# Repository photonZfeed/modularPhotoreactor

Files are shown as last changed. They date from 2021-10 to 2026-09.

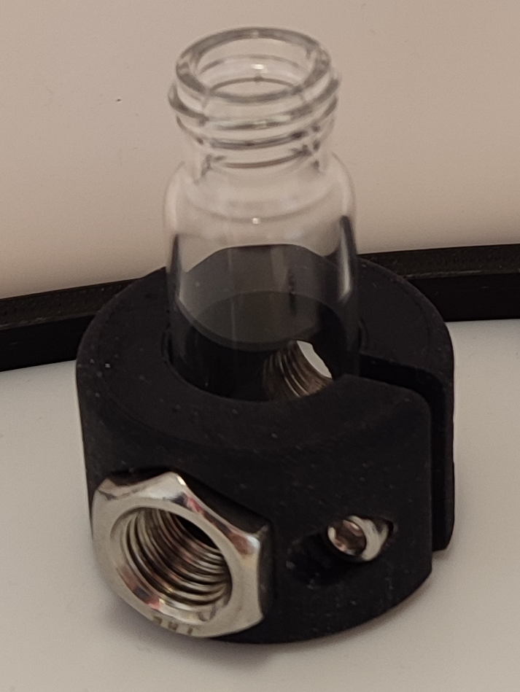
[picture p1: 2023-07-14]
01_CAD/03_Multi_Batch_Screening_Photoreactor/00_Indirect_Irradiation_Module/04_Accesories/00_UV_Vis_Cell_4mL_GC_Vial/UV_vis_cell_4mL_GC_vial_SLA.png

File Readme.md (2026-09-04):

# modularPhotoreactor

A modular and characterized open source photoreactor and the mutli-batch screening phototreactor extension

## Documentation

The assembly of the devices is documented in the [CAD section](./01_CAD/).

See also the 3D-pdfs for detailed assembly instructions in the [assembly section](./03_ASSEMBLY_INSTRUCTIONS/).

The Python modules for the operation of the reactor controller are documented in the repository [Py4ModPhotoreactor](https://github.com/photonZfeed/Py4ModPhotoreactor). See also the fairly detailed docstrings in the code. 

## Folder Structure

```
📦HARDWARE_Modular_Photoreactor
┣ 📂 01_CAD
┃  ┣ 📂 00_Corpus
┃  ┃  ┣ 📂 00_Corpus_90x90x100mm
┃  ┃  ┃  ┣ 📂 00_corpus
┃  ┃  ┃  ┃  ┣ 📜 corpus_90x90x100mm_back_wall.stl
┃  ┃  ┃  ┃  ┣ 📜 corpus_90x90x100mm_front_wall.stl
┃  ┃  ┃  ┃  ┣ 📜 corpus_90x90x100mm_side_walls.stl
┃  ┃  ┃  ┃  ┣ 📜 corpus_90x90x100mm_side_walls_LED_holder.stl
┃  ┃  ┃  ┃  ┣ 📜 corpus_cover.stl
┃  ┃  ┃  ┃  ┗ 📜 corpus_stand.stl
┃  ┃  ┃  ┣ 📂 01_irradiation_module
┃  ┃  ┃  ┃  ┣ 📜 20210104_Thorlabsl_modul.stl
┃  ┃  ┃  ┃  ┣ 📜 corpus_90x90mm_irrad_Max350.stl
┃  ┃  ┃  ┃  ┣ 📜 corpus_90x90mm_irrad_Max350_adapter.stl
┃  ┃  ┃  ┃  ┣ 📜 corpus_90x90mm_irrad_starcool.stl
┃  ┃  ┃  ┃  ┣ 📜 corpus_90x90mm_irrad_Thorlabs.stl
┃  ┃  ┃  ┃  ┣ 📜 corpus_90x90mm_irrad_Thorlabs_adapter.stl
┃  ┃  ┃  ┃  ┗ 📜 corpus_90x90mm_irrad_Thorlabs_collimator.stl
┃  ┃  ┃  ┣ 📂 02_stirring_module
┃  ┃  ┃  ┃  ┣ 📜 corpus_90x90mm_stirring_module.stl
┃  ┃  ┃  ┃  ┣ 📜 corpus_90x90mm_stirring_module_holder_electric_motor.stl
┃  ┃  ┃  ┃  ┣ 📜 corpus_90x90mm_stirring_module_magnet_holder.stl
┃  ┃  ┃  ┃  ┗ 📜 corpus_90x90mm_stirring_module_magnet_holder_blind_plug.stl
┃  ┃  ┃  ┗ 📂 03_sample_holders
┃  ┃  ┃     ┣ 📜 corpus_90x90mm_11mL_Biotage_MWvial_6S_alignment_holder.stl
┃  ┃  ┃     ┣ 📜 corpus_90x90mm_11mL_Biotage_MWvial_6S_holder.stl
┃  ┃  ┃     ┣ 📜 corpus_90x90mm_4mL_GCvial_ND13_10S_alignment_holder.stl
┃  ┃  ┃     ┣ 📜 corpus_90x90mm_4mL_GCvial_ND13_10S_holder.stl
┃  ┃  ┃     ┣ 📜 corpus_90x90mm_4mL_GCvial_ND13_1S_alignment_holder.stl
┃  ┃  ┃     ┣ 📜 corpus_90x90mm_4mL_GCvial_ND13_1S_holder.stl
┃  ┃  ┃     ┣ 📜 corpus_90x90mm_4mL_GCvial_ND13_4S_alignment_holder.stl
┃  ┃  ┃     ┣ 📜 corpus_90x90mm_4mL_GCvial_ND13_4S_holder.stl
┃  ┃  ┃     ┣ 📜 corpus_90x90mm_4mL_GCvial_ND13_6S_alignment_holder.stl
┃  ┃  ┃     ┣ 📜 corpus_90x90mm_4mL_GCvial_ND13_6S_holder.stl
┃  ┃  ┃     ┣ 📜 corpus_90x90mm_4mL_GCvial_ND13_8S_alignment_holder.stl
┃  ┃  ┃     ┣ 📜 corpus_90x90mm_4mL_GCvial_ND13_8S_holder.stl
┃  ┃  ┃     ┣ 📜 corpus_90x90mm_8mL_GCvial_ND13_10S_alignment_holder.stl
┃  ┃  ┃     ┗ 📜 corpus_90x90mm_8mL_GCvial_ND13_1S_alignment_holder.stl
┃  ┃  ┣ 📂 01_Corpus_90x90x140mm
┃  ┃  ┃  ┣ 📂 00_corpus
┃  ┃  ┃  ┃  ┣ 📜 corpus_90x90x140mm_back_wall.stl
┃  ┃  ┃  ┃  ┣ 📜 corpus_90x90x140mm_front_wall.stl
┃  ┃  ┃  ┃  ┣ 📜 corpus_90x90x140mm_side_walls.stl
┃  ┃  ┃  ┃  ┣ 📜 corpus_cover.stl
┃  ┃  ┃  ┃  ┗ 📜 corpus_stand.stl
┃  ┃  ┃  ┣ 📂 01_irradiation_module
┃  ┃  ┃  ┃  ┣ 📜 20210104_Thorlabsl_modul.stl
┃  ┃  ┃  ┃  ┣ 📜 corpus_90x90mm_irrad_Max350.stl
┃  ┃  ┃  ┃  ┣ 📜 corpus_90x90mm_irrad_Max350_adapter.stl
┃  ┃  ┃  ┃  ┣ 📜 corpus_90x90mm_irrad_starcool.stl
┃  ┃  ┃  ┃  ┣ 📜 corpus_90x90mm_irrad_Thorlabs.stl
┃  ┃  ┃  ┃  ┣ 📜 corpus_90x90mm_irrad_Thorlabs_adapter.stl
┃  ┃  ┃  ┃  ┗ 📜 corpus_90x90mm_irrad_Thorlabs_collimator.stl
┃  ┃  ┃  ┣ 📂 02_stirring_module
┃  ┃  ┃  ┃  ┣ 📜 corpus_90x90mm_stirring_module.stl
┃  ┃  ┃  ┃  ┣ 📜 corpus_90x90mm_stirring_module_holder_electric_motor.stl
┃  ┃  ┃  ┃  ┣ 📜 corpus_90x90mm_stirring_module_magnet_holder.stl
┃  ┃  ┃  ┃  ┗ 📜 corpus_90x90mm_stirring_module_magnet_holder_blind_plug.stl
┃  ┃  ┃  ┗ 📂 03_sample_holders
┃  ┃  ┃     ┣ 📜 corpus_90x90mm_11mL_Biotage_MWvial_6S_alignment_holder.stl
┃  ┃  ┃     ┣ 📜 corpus_90x90mm_11mL_Biotage_MWvial_6S_holder.stl
┃  ┃  ┃     ┣ 📜 corpus_90x90mm_4mL_GCvial_ND13_10S_alignment_holder.stl
┃  ┃  ┃     ┣ 📜 corpus_90x90mm_4mL_GCvial_ND13_10S_holder.stl
┃  ┃  ┃     ┣ 📜 corpus_90x90mm_4mL_GCvial_ND13_1S_alignment_holder.stl
┃  ┃  ┃     ┣ 📜 corpus_90x90mm_4mL_GCvial_ND13_1S_holder.stl
┃  ┃  ┃     ┣ 📜 corpus_90x90mm_4mL_GCvial_ND13_4S_alignment_holder.stl
┃  ┃  ┃     ┣ 📜 corpus_90x90mm_4mL_GCvial_ND13_4S_holder.stl
┃  ┃  ┃     ┣ 📜 corpus_90x90mm_4mL_GCvial_ND13_6S_alignment_holder.stl
┃  ┃  ┃     ┣ 📜 corpus_90x90mm_4mL_GCvial_ND13_6S_holder.stl
┃  ┃  ┃     ┣ 📜 corpus_90x90mm_4mL_GCvial_ND13_8S_alignment_holder.stl
┃  ┃  ┃     ┣ 📜 corpus_90x90mm_4mL_GCvial_ND13_8S_holder.stl
┃  ┃  ┃     ┣ 📜 corpus_90x90mm_8mL_GCvial_ND13_10S_alignment_holder.stl
┃  ┃  ┃     ┗ 📜 corpus_90x90mm_8mL_GCvial_ND13_1S_alignment_holder.stl
┃  ┃  ┗ 📂 02_Corpus_130x130x130mm
┃  ┃     ┣ 📂 00_corpus
┃  ┃     ┃  ┣ 📜 corpus130x130mm_side_walls.stl
┃  ┃     ┃  ┣ 📜 corpus_130x130mm_back_wall.stl
┃  ┃     ┃  ┣ 📜 corpus_130x130mm_cover.stl
┃  ┃     ┃  ┣ 📜 corpus_130x130mm_front_wall_monting_thermal_hose.stl
┃  ┃     ┃  ┣ 📜 corpus_130x130mm_side_wall_left.stl
┃  ┃     ┃  ┣ 📜 corpus_130x130mm_side_wall_right.stl
┃  ┃     ┃  ┣ 📜 corpus_130x130mm_stand_20mm.stl
┃  ┃     ┃  ┣ 📜 fin_back_wall.stl
┃  ┃     ┃  ┣ 📜 fin_front_wall.stl
┃  ┃     ┃  ┣ 📜 spacer_side_walls_5mm.stl
┃  ┃     ┃  ┗ 📜 spacer_stand_5mm.stl
┃  ┃     ┣ 📂 01_irradiation_module
┃  ┃     ┃  ┗ 📜 irrad_module.stl
┃  ┃     ┣ 📂 02_sample_holders
┃  ┃     ┃  ┣ 📜 corpus_130x130mm_GCvial_ND13_18S_alignment_holder.stl
┃  ┃     ┃  ┣ 📜 corpus_130x130mm_GCvial_ND13_18S_holder.stl
┃  ┃     ┃  ┣ 📜 corpus_130x130mm_GCvial_ND13_1S_alignment_holder.stl
┃  ┃     ┃  ┗ 📜 corpus_130x130mm_GCvial_ND13_1S_holder.stl
┃  ┃     ┗ 📂 03_tempering_module
┃  ┃        ┣ 📜 back_mounting_thermo_hose.stl
┃  ┃        ┣ 📜 fan_holder.stl
┃  ┃        ┣ 📜 holder_tempering_module.stl
┃  ┃        ┣ 📜 mounting_alu_water_cooler.stl
┃  ┃        ┗ 📜 spacer_holder_tempering_module.stl
┃  ┣ 📂 01_controller
┃  ┃  ┣ 📜 controller_case.stl
┃  ┃  ┣ 📜 controller_case_LCD_holder.stl
┃  ┃  ┗ 📜 controller_electronic_board_holder.stl
┃  ┣ 📂 02_Peripheral_Modules
┃  ┃  ┣ 📂 00_ambient_temperature
┃  ┃  ┃  ┣ 📜 base_plate_ambient_temperature_extension.stl
┃  ┃  ┃  ┗ 📜 case_ambient_temperature_extension.stl
┃  ┃  ┣ 📂 01_tempering_extension
┃  ┃  ┃  ┣ 📜 base_plate.stl
┃  ┃  ┃  ┗ 📜 case_tempering_extension.stl
┃  ┃  ┣ 📂 02_master_extension
┃  ┃  ┃  ┣ 📜 base_plate.stl
┃  ┃  ┃  ┗ 📜 case_master_extension.stl
┃  ┃  ┣ 📂 03_membrane_pump_extension
┃  ┃  ┃  ┣ 📜 base_plate_membrane_pump.stl
┃  ┃  ┃  ┣ 📜 base_plate_membrane_pump_exension.stl
┃  ┃  ┃  ┣ 📜 case_membrane_pump.stl
┃  ┃  ┃  ┗ 📜 case_membrane_pump_extension.stl
┃  ┃  ┗ 📂 04_pressure_sensor_extension
┃  ┃     ┣ 📜 base_plate.stl
┃  ┃     ┣ 📜 base_plate_updated.stl
┃  ┃     ┣ 📜 case_pressure_extension.stl
┃  ┃     ┗ 📜 case_pressure_extension_updated.stl
┃  ┣ 📂 03_Multi_Batch_Screening_Photoreactor
┃  ┃  ┣ 📂 00_Indirect_Irradiation_Module
┃  ┃  ┃  ┣ 📂 00_Base_Module
┃  ┃  ┃  ┃  ┗ 📜 Base_Module.stl
┃  ┃  ┃  ┣ 📂 01_Irradiation_Module
┃  ┃  ┃  ┃  ┣ 📜 300mm_alu_heatsink.stl
┃  ┃  ┃  ┃  ┣ 📜 heatsink_holder_left.stl
┃  ┃  ┃  ┃  ┣ 📜 heatsink_holder_right.stl
┃  ┃  ┃  ┃  ┗ 📜 stand_irradiation_module.stl
┃  ┃  ┃  ┣ 📂 02_Reflector_Module
┃  ┃  ┃  ┃  ┣ 📜 PTFE_Side_Wall.stl
┃  ┃  ┃  ┃  ┣ 📜 Reflector_Holder_Nut.stl
┃  ┃  ┃  ┃  ┗ 📜 Reflector_Holder_Screw.stl
┃  ┃  ┃  ┣ 📂 03_Mobile_Cover
┃  ┃  ┃  ┃  ┣ 📜 back.stl
┃  ┃  ┃  ┃  ┣ 📜 connector.stl
┃  ┃  ┃  ┃  ┣ 📜 front.stl
┃  ┃  ┃  ┃  ┣ 📜 sides.stl
┃  ┃  ┃  ┃  ┗ 📜 top.stl
┃  ┃  ┃  ┗ 📂 04_Accesories
┃  ┃  ┃     ┗ 📂 00_UV_Vis_Cell_4mL_GC_Vial
┃  ┃  ┃        ┣ 📜 UV_vis_cell_4mL_GC_vial_SLA.png
┃  ┃  ┃        ┗ 📜 UV_vis_cell_4mL_GC_vial_SLA.stl
┃  ┃  ┗ 📂 01_Direct_Irradiation_Module
┃  ┃     ┣ 📂 00_reflector_fixed_height
┃  ┃     ┃  ┣ 📜 corner_pillar_1.stl
┃  ┃     ┃  ┣ 📜 corner_pillar_2.stl
┃  ┃     ┃  ┣ 📜 corner_pillar_3.stl
┃  ┃     ┃  ┣ 📜 corner_pillar_4.stl
┃  ┃     ┃  ┣ 📜 corner_pillar_connector_330mm.stl
┃  ┃     ┃  ┣ 📜 corner_pillar_connector_350mm.stl
┃  ┃     ┃  ┣ 📜 corner_pillar_support.stl
┃  ┃     ┃  ┣ 📜 heatsink_holder_female.stl
┃  ┃     ┃  ┣ 📜 heatsink_holder_male.stl
┃  ┃     ┃  ┣ 📜 holder_feet.stl
┃  ┃     ┃  ┣ 📜 holder_feet_assembly.stl
┃  ┃     ┃  ┣ 📜 holder_feet_support.stl
┃  ┃     ┃  ┣ 📜 reflector_fixed_height_assembly.stl
┃  ┃     ┃  ┗ 📜 reflector_holder.stl
┃  ┃     ┣ 📂 01_modular_reflector_adjustable_height
┃  ┃     ┃  ┣ 📜 corner_reflector_holder_1a.stl
┃  ┃     ┃  ┣ 📜 corner_reflector_holder_1b.stl
┃  ┃     ┃  ┣ 📜 modular_reflector_assembly.stl
┃  ┃     ┃  ┣ 📜 reflector_holder_330mm_1cm.stl
┃  ┃     ┃  ┣ 📜 reflector_holder_330mm_2cm.stl
┃  ┃     ┃  ┣ 📜 reflector_holder_330mm_6cm.stl
┃  ┃     ┃  ┣ 📜 reflector_holder_350mm_1cm.stl
┃  ┃     ┃  ┣ 📜 reflector_holder_350mm_2cm.stl
┃  ┃     ┃  ┗ 📜 reflector_holder_350mm_6cm.stl
┃  ┃     ┗ 📂 02_heatsink_and _LED_mounting_plate
┃  ┃        ┣ 📜 heatsink_200x200.stl
┃  ┃        ┗ 📜 LED_mount_400x400.stl
┃  ┗ 📜 readme.md
┣ 📂 02_MATERIALS
┃  ┣ 📂 00_electronics
┃  ┃  ┣ 📂 00_Tinkerforge
┃  ┃  ┃  ┗ 📜 Tinkerforge.txt
┃  ┃  ┣ 📂 01_LEDs
┃  ┃  ┃  ┣ 📂 blue
┃  ┃  ┃  ┃  ┣ 📂 453nm
┃  ┃  ┃  ┃  ┃  ┗ 📜 LZ4-00B208-0000.txt
┃  ┃  ┃  ┃  ┣ 📂 455nm
┃  ┃  ┃  ┃  ┃  ┗ 📜 LST1-01F06-RYL1-00.txt
┃  ┃  ┃  ┃  ┗ 📂 460nm
┃  ┃  ┃  ┃     ┣ 📜 5412869-LED_2520Engin_Datasheet_LuxiGen_LZ1-00DB00-1532005.pdf
┃  ┃  ┃  ┃     ┗ 📜 LZ1-00DB00.txt
┃  ┃  ┃  ┣ 📂 green
┃  ┃  ┃  ┃  ┗ 📂 530nm
┃  ┃  ┃  ┃     ┗ 📜 LST1-01F06-GRN1-00.txt
┃  ┃  ┃  ┣ 📂 RGBA
┃  ┃  ┃  ┃  ┗ 📜 LZ4-20MA00-0000.txt
┃  ┃  ┃  ┗ 📂 UV
┃  ┃  ┃     ┣ 📂 365nm
┃  ┃  ┃     ┃  ┗ 📜 LST1-01G01-UV01-00.txt
┃  ┃  ┃     ┣ 📂 385nm
┃  ┃  ┃     ┃  ┗ 📜 LZ1-10UB00-01U4.txt
┃  ┃  ┃     ┗ 📂 405nm
┃  ┃  ┃        ┣ 📂 onecore
┃  ┃  ┃        ┃  ┗ 📜 LZ1-10UB00-01U7.txt
┃  ┃  ┃        ┗ 📂 quadcore
┃  ┃  ┃           ┗ 📜 LZ4-V0UB0R-00U8.txt
┃  ┃  ┣ 📂 02_raspberry_pi
┃  ┃  ┃  ┗ 📜 raspberry_pi_4_8GB.txt
┃  ┃  ┣ 📂 03_sd_card
┃  ┃  ┃  ┗ 📜 SD_card.txt
┃  ┃  ┣ 📂 04_peltier_element
┃  ┃  ┃  ┗ 📜 peltier.txt
┃  ┃  ┣ 📂 05_power_supplies
┃  ┃  ┃  ┣ 📂 00_12V_5A
┃  ┃  ┃  ┃  ┗ 📜 12V_5A.txt
┃  ┃  ┃  ┗ 📂 00_24V_6A
┃  ┃  ┃     ┗ 📜 24V_6A.txt
┃  ┃  ┣ 📂 06_small_parts
┃  ┃  ┃  ┣ 📂 00_stripboard
┃  ┃  ┃  ┃  ┗ 📜 stripboard_WR_914-HP.txt
┃  ┃  ┃  ┣ 📂 01_connection_jacks
┃  ┃  ┃  ┃  ┣ 📜 2Pin_PCB_Mount_2.5mm_Pitch.txt
┃  ┃  ┃  ┃  ┣ 📜 2Pin_PCB_Mount_5mm_Pitch.txt
┃  ┃  ┃  ┃  ┣ 📜 banana_plug_female.txt
┃  ┃  ┃  ┃  ┣ 📜 banana_plug_male.txt
┃  ┃  ┃  ┃  ┣ 📜 Cable_extension_PWM_4-Pin_Moltex.txt
┃  ┃  ┃  ┃  ┣ 📜 DC_Jack.txt
┃  ┃  ┃  ┃  ┗ 📜 wago_2Conductur_clamp.txt
┃  ┃  ┃  ┣ 📂 02_Stacking_Header_Raspberry_Pi
┃  ┃  ┃  ┃  ┗ 📜 Stacking_Header_Raspberry_Pi.txt
┃  ┃  ┃  ┣ 📂 03_two_position_switch
┃  ┃  ┃  ┃  ┗ 📜 two_position_switch.txt
┃  ┃  ┃  ┗ 📂 04_silicone_wire
┃  ┃  ┃     ┗ 📜 silicone_wire.txt
┃  ┃  ┣ 📂 07_LED_drivers
┃  ┃  ┃  ┣ 📜 350mA_driver.txt
┃  ┃  ┃  ┣ 📜 500mA_driver.txt
┃  ┃  ┃  ┗ 📜 700mA_driver.txt
┃  ┃  ┣ 📂 08_membrane_pump
┃  ┃  ┃  ┣ 📜 accessories_membrane_pump.txt
┃  ┃  ┃  ┗ 📜 Membrane_Pump.txt
┃  ┃  ┗ 📂 09_fans
┃  ┃     ┣ 📂 00_fan_corpus_90x90mm
┃  ┃     ┃  ┗ 📜 fan.txt
┃  ┃     ┣ 📂 01_fan_corpus_130x130mm
┃  ┃     ┃  ┣ 📜 fan.txt
┃  ┃     ┃  ┗ 📜 fan_update.txt
┃  ┃     ┣ 📂 02_power_supply_fan_corpus_90x90mm
┃  ┃     ┃  ┗ 📜 power_supply.txt
┃  ┃     ┗ 📂 03_Pi_Fan
┃  ┃        ┗ 📜 Pi_Fan.txt
┃  ┣ 📂 01_accessories
┃  ┃  ┣ 📂 00_thermal_tube
┃  ┃  ┃  ┗ 📜 thermal_hose.txt
┃  ┃  ┣ 📂 01_hose_clamps
┃  ┃  ┃  ┗ 📜 hose_clamp.txt
┃  ┃  ┣ 📂 02_screws_nuts
┃  ┃  ┃  ┣ 📂 00_M3_Set
┃  ┃  ┃  ┃  ┗ 📜 M3_screw_set.txt
┃  ┃  ┃  ┣ 📂 01_Nylon_Spacer
┃  ┃  ┃  ┃  ┗ 📜 nylon_spacer.txt
┃  ┃  ┃  ┣ 📂 02_M3_60mm
┃  ┃  ┃  ┃  ┗ 📜 M3_60mm.txt
┃  ┃  ┃  ┗ 📂 02_M3_70mm
┃  ┃  ┃     ┗ 📜 M3_70mm.txt
┃  ┃  ┣ 📂 03_cooler
┃  ┃  ┃  ┣ 📂 00_tempering_module_cooler
┃  ┃  ┃  ┃  ┣ 📂 00_pelltier_cooler
┃  ┃  ┃  ┃  ┃  ┗ 📜 Alpine AM4 Passive.txt
┃  ┃  ┃  ┃  ┗ 📂 01_alu_water_cooler
┃  ┃  ┃  ┃     ┗ 📜 alu_water_cooler.txt
┃  ┃  ┃  ┗ 📂 01_LED_cooler
┃  ┃  ┃     ┣ 📂 00_25mm_cooler
┃  ┃  ┃     ┃  ┗ 📜 sink_s-1265491.txt
┃  ┃  ┃     ┣ 📂 01_50mm_cooler
┃  ┃  ┃     ┃  ┗ 📜 sink_s-1265491.txt
┃  ┃  ┃     ┗ 📂 02_300mm_cooler
┃  ┃  ┃        ┗ 📜 ATS-EXL75-300-R0.txt
┃  ┃  ┣ 📂 04_foam_rubber_seal
┃  ┃  ┃  ┗ 📜 foam_rubber_seal.txt
┃  ┃  ┗ 📂 05_PTFE
┃  ┃     ┣ 📂 00_technical_PTFE
┃  ┃     ┃  ┗ 📜 technical_PTFE.txt
┃  ┃     ┗ 📂 01_optical_PTFE
┃  ┃        ┗ 📜 optical_PTFE.txt
┃  ┗ 📜 readme.md
┣ 📂 03_ASSEMBLY_INSTRUCTIONS
┃  ┣ 📂 00_Corpus
┃  ┃  ┣ 📜 Assembly_Photoreactor_Corpus_130x130x130mm.pdf
┃  ┃  ┣ 📜 Assembly_Photoreactor_Corpus_90x90x140mm.pdf
┃  ┃  ┗ 📜 Assembly_Photoreactor_Corpus_90x90x90mm.pdf
┃  ┣ 📂 01_Controller
┃  ┃  ┣ 📜 20211029_Stripboard_drill_holes.pdf
┃  ┃  ┣ 📜 Controller_circuit_diagram.pdf
┃  ┃  ┣ 📜 Controller_Documentation.pdf
┃  ┃  ┗ 📜 Logic_Controller.pdf
┃  ┣ 📂 02_Peripheral_Modules
┃  ┃  ┣ 📂 00_Tempering_Module
┃  ┃  ┃  ┗ 📜 Peltier_Circuit_Diagram.pdf
┃  ┃  ┗ 📂 01_LED_Driver_Module
┃  ┃     ┗ 📜 LED Driver Module.pdf
┃  ┣ 📂 03_Irradiation_Module
┃  ┃  ┗ 📜 assembly_instruction_LED_cooler.pdf
┃  ┣ 📂 04_Multi_Batch_Screening_Phororeactor
┃  ┃  ┣ 📂 00_Photoreactor
┃  ┃  ┃  ┗ 📜 Multi_Batch_Screening_Photoreactor_assembly.pdf
┃  ┃  ┗ 📂 01_Mobile_Cover
┃  ┃     ┣ 📜 Mobile_Cover_assembly.pdf
┃  ┃     ┗ 📜 Mobile_Cover_assembly.stl
┃  ┗ 📜 readme.md
┣ 📂 04_IMAGES
┃  ┣ 📜 Licenses.png
┃  ┗ 📜 Licenses.svg
┣ 📜 License.md
┗ 📜 Readme.md
```

## More Information

<!--- Cite this repository: [![DOI](https://zenodo.org/badge/368164449.svg)](https://zenodo.org/badge/latestdoi/368164449) --->

## Publications

### Core Modular Photoreactor Platform

* **2022**  
  Kowalczyk et al.  
  *Making Photocatalysis Comparable Using a Modular and Characterized Open-Source Photoreactor*  
  ChemPhotoChem, 6 (2022).  
  https://doi.org/10.1002/cptc.202200044

* **2023**  
  Kowalczyk et al.  
  *Making Photocatalysts Screenable – A Milli-Scale Multi-Batch Screening Photoreactor as Extension for the Modular Photoreactor*  
  Reaction Chemistry & Engineering (2023).  
  https://doi.org/10.1039/D3RE00398A

### Related Preprints

* **2025**  
  Koba et al.  
  *Improving Efficiency of Light-Driven Water Oxidation Catalysis through Dynamic Irradiation*  
  To be submitted (2025).  
  https://doi.org/10.5281/zenodo.17867915

* **2025**  
  Wiedemann et al.  
  *Making Photocatalyst Screening Photoefficient – Combining Radiation Field Models to Design a Direct Irradiation Module for the Multi-Batch Screening Reactor*  
  To be submitted (2025).  
  https://doi.org/10.5281/zenodo.17867874
  
### Related Journal Articles

* **2022**  
  Buday et al.  
  *Activating a [FeFe] Hydrogenase Mimic for Hydrogen Evolution under Visible Light*  
  Angewandte Chemie International Edition (2022).  
  https://doi.org/10.1002/anie.202202079

* **2023**  
  Knorr et al.  
  *Unlocking the potential of ketocoumarins: efficient photosensitizers for sustainable light-driven hydrogen evolution*  
  Journal of Materials Chemistry A (2023).  
  https://doi.org/10.1039/D3TA04450E

* **2023**  
  Çeper et al.  
  *Visible-Light-Driven Hydrogen Evolution of PtNP/[Ru(bpy)3]2+/Polyampholyte Hybrid Hydrogels*  
  ACS Applied Polymer Materials (2023).  
  https://doi.org/10.1021/acsapm.3c01051

* **2023**  
  Abbas et al.  
  *Initial Quenching Efficiency Determines Light-Driven H2 Evolution of [Mo3S13]2− in Lipid Bilayers*  
  Chemistry – A European Journal (2023).  
  https://doi.org/10.1002/chem.202302284

* **2024**  
  Çeper et al.  
  *Noble Metal-Free Light-Driven Hydrogen Evolution Catalysis in Polyampholytic Hydrogel Networks*  
  ACS Applied Materials & Interfaces (2024).  
  https://doi.org/10.1021/acsami.4c04045

* **2024**  
  Kasahara et al.  
  *Molecular Dyad vs Multi-Component Approach – Photocatalytic Hydrogen Evolution by Combining Oligothiophene Photosensitizers with [FeFe]-Hydrogenase Mimics*  
  ChemCatChem (2024).  
  https://doi.org/10.1002/cctc.202400247

* **2025**  
  Kasahara et al.  
  *[FeFe]-Hydrogenase Mimic with Organic Photosensitizers for Long-Lived Excited States and Efficient Photocatalytic H2 Production*  
  Cell Reports Physical Science (2025).  
  https://doi.org/10.1016/j.xcrp.2025.102975

* **2025**  
  Basma et al.  
  *Engineered [FeFe]-Hydrogenase Mimics Featuring Heteroaryl Linkers: Molecular Design and Photocatalytic Hydrogen Evolution under Visible Light*  
  Inorganic Chemistry Frontiers (2025).  
  https://doi.org/10.1039/D5QI01191D

* **2025**  
  Abbas et al.  
  *Selective Light-Driven CO2 to CO Reduction by a [FeFe]-Hydrogenase Mimic in Water*  
  ChemCatChem (2025).  
  https://doi.org/10.1002/cctc.202401947

* **2025**  
  Mandal et al.  
  *Mn2+ and [Ru(bpy)3]2+ in UiO-67 Metal-Organic Frameworks Enhance Photocatalytic Oxidation of Benzylamine via an Electron Transfer Pathway*  
  RSC Advances (2025).  
  https://doi.org/10.1039/D5RA04503G

* **2025**  
  Mandal et al.  
  *Enhanced and Durable Light-Driven Hydrogen Evolution by Cobalt-Based Prussian Blue Analogs in Phospholipid Bilayers*  
  Advanced Energy and Sustainability Research (2025).  
  https://doi.org/10.1002/aesr.202400372

* **2025**  
  Mandal et al.  
  *The Zr8O6 Secondary Building Unit and Porphyrin Linker Catalyze Light-Driven H2 Evolution in Porphyrin-Based Metal-Organic Frameworks*  
  ChemSusChem (2025).  
  https://doi.org/10.1002/cssc.202500372

* **2026**  
  Kolbinger et al.  
  *{Mo2} can do it too: dynamic irradiation increases photonic efficiency of light-driven hydrogen evolution by [Mo2S12]2−*  
  Sustainable Energy & Fuels (2026).  
  https://doi.org/10.1039/D6SE00078A

* **2026**  
  Kolbinger et al.  
  *Fewer photons, more hydrogen: effects of dynamic irradiation on light-driven hydrogen evolution by thiomolybdate catalysts*  
  Sustainable Energy & Fuels (2026).  
  https://doi.org/10.1039/D5SE01490E

* **2026**  
  Brezhneva et al.  
  *Insights Into Overall Photocatalytic Water Splitting Through Simultaneous In Situ H2 and O2 Measurements*  
  ChemSusChem (2026).  
  https://doi.org/10.1002/cssc.202502721

* **2026**  
  Tombrink et al.  
  *4CzIPN Photosensitizes the Cobaloxime-Catalyzed Light-Driven Hydrogen Evolution Reaction*  
  ChemSusChem (2026).  
  https://doi.org/10.1002/cssc.70942

* **2026**  
  Baumgarten et al.  
  *Phenothiazine redox mediators boost photocatalytic hydrogen evolution*  
  EES Catalysis (2026).  
  https://doi.org/10.1039/D6EY00029K

* **2026**  
  Utievskyi et al.  
  *Embedding a Dinuclear Ru–Pt Photocatalyst Into Polyampholytic Graft Copolymer Matrix Enables Prolonged Hydrogen Evolution While Allowing Catalyst Repair*  
  Chemistry – A European Journal (2026).  
  https://doi.org/10.1002/chem.71568

* **2026**  
  Schleicher et al.  
  *Light-driven hydrogen evolution reactivity of molecular thio-oxomolybdate catalysts*  
  Sustainable Energy & Fuels (2026).  
  https://doi.org/10.1039/D6SE00061D

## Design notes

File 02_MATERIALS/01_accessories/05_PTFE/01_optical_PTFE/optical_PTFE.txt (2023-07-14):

Hersteller/Manufacturer: 	Berghof Fluoroplastics
Herstellerreferenz/Manufacturer reference PTFE 2 mm: OPF200.XXX.500-U	 	
Verkäufer/Supplier: Berghof Fluoroplastics
link: https://www.berghof-fluoroplastics.com/produkte/optopolymerr-optische-materialloesungen/folien
link data sheet: https://www.berghof-fluoroplastics.com/fileadmin/redaktion-bft/Downloads/03_Optisches_PTFE_-_Optopolymer_R_/BFT_Optopolymer_DE_2_.pdf

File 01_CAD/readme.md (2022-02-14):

# Directory Structure
```
📦01_CAD
 ┣ 📂00_Corpus
 ┃ ┣ 📂00_Corpus_90x90x100mm
 ┃ ┃ ┣ 📂00_corpus
 ┃ ┃ ┃ ┣ 📜corpus_90x90x100mm_back_wall.stl
 ┃ ┃ ┃ ┣ 📜corpus_90x90x100mm_front_wall.stl
 ┃ ┃ ┃ ┣ 📜corpus_90x90x100mm_side_walls.stl
 ┃ ┃ ┃ ┣ 📜corpus_90x90x100mm_side_walls_LED_holder.stl
 ┃ ┃ ┃ ┣ 📜corpus_cover.stl
 ┃ ┃ ┃ ┣ 📜corpus_stand.stl
 ┃ ┃ ┣ 📂01_irradiation_module
 ┃ ┃ ┃ ┣ 📜corpus_90x90mm_irrad_Max350.stl
 ┃ ┃ ┃ ┣ 📜corpus_90x90mm_irrad_Max350_adapter.stl
 ┃ ┃ ┃ ┣ 📜corpus_90x90mm_irrad_starcool.stl
 ┃ ┃ ┃ ┣ 📜corpus_90x90mm_irrad_Thorlabs.stl
 ┃ ┃ ┃ ┣ 📜corpus_90x90mm_irrad_Thorlabs_adapter.stl
 ┃ ┃ ┃ ┣ 📜corpus_90x90mm_irrad_Thorlabs_collimator.stl
 ┃ ┃ ┣ 📂02_stirring_module
 ┃ ┃ ┃ ┣ 📜corpus_90x90mm_stirring_module.stl
 ┃ ┃ ┃ ┣ 📜corpus_90x90mm_stirring_module_holder_electric_motor.stl
 ┃ ┃ ┃ ┣ 📜corpus_90x90mm_stirring_module_magnet_holder.stl
 ┃ ┃ ┃ ┣ 📜corpus_90x90mm_stirring_module_magnet_holder_blind_plug.stl
 ┃ ┃ ┗ 📂03_sample_holders
 ┃ ┃ ┃ ┣ 📜corpus_90x90mm_4mL_GCvial_ND13_10S_alignment_holder.stl
 ┃ ┃ ┃ ┣ 📜corpus_90x90mm_4mL_GCvial_ND13_10S_holder.stl
 ┃ ┃ ┃ ┣ 📜corpus_90x90mm_4mL_GCvial_ND13_1S_alignment_holder.stl
 ┃ ┃ ┃ ┣ 📜corpus_90x90mm_4mL_GCvial_ND13_1S_holder.stl
 ┃ ┃ ┃ ┣ 📜corpus_90x90mm_4mL_GCvial_ND13_4S_alignment_holder.stl
 ┃ ┃ ┃ ┣ 📜corpus_90x90mm_4mL_GCvial_ND13_4S_holder.stl
 ┃ ┃ ┃ ┣ 📜corpus_90x90mm_4mL_GCvial_ND13_6S_alignment_holder.stl
 ┃ ┃ ┃ ┣ 📜corpus_90x90mm_4mL_GCvial_ND13_6S_holder.stl
 ┃ ┃ ┃ ┣ 📜corpus_90x90mm_4mL_GCvial_ND13_8S_alignment_holder.stl
 ┃ ┃ ┃ ┣ 📜corpus_90x90mm_4mL_GCvial_ND13_8S_holder.stl
 ┃ ┣ 📂01_Corpus_90x90x140mm
 ┃ ┃ ┣ 📂00_corpus
 ┃ ┃ ┃ ┣ 📜corpus_90x90x140mm_back_wall.stl
 ┃ ┃ ┃ ┣ 📜corpus_90x90x140mm_front_wall.stl
 ┃ ┃ ┃ ┣ 📜corpus_90x90x140mm_side_walls.stl
 ┃ ┃ ┃ ┣ 📜corpus_cover.stl
 ┃ ┃ ┃ ┣ 📜corpus_stand.stl
 ┃ ┃ ┣ 📂01_irradiation_module
 ┃ ┃ ┃ ┣ 📜corpus_90x90mm_irrad_Max350.stl
 ┃ ┃ ┃ ┣ 📜corpus_90x90mm_irrad_Max350_adapter.stl
 ┃ ┃ ┃ ┣ 📜corpus_90x90mm_irrad_starcool.stl
 ┃ ┃ ┃ ┣ 📜corpus_90x90mm_irrad_Thorlabs.stl
 ┃ ┃ ┃ ┣ 📜corpus_90x90mm_irrad_Thorlabs_adapter.stl
 ┃ ┃ ┃ ┣ 📜corpus_90x90mm_irrad_Thorlabs_collimator.stl
 ┃ ┃ ┣ 📂02_stirring_module
 ┃ ┃ ┃ ┣ 📜corpus_90x90mm_stirring_module.stl
 ┃ ┃ ┃ ┣ 📜corpus_90x90mm_stirring_module_holder_electric_motor.stl
 ┃ ┃ ┃ ┣ 📜corpus_90x90mm_stirring_module_magnet_holder.stl
 ┃ ┃ ┃ ┣ 📜corpus_90x90mm_stirring_module_magnet_holder_blind_plug.stl
 ┃ ┃ ┗ 📂03_sample_holders
 ┃ ┃ ┃ ┣ 📜corpus_90x90mm_4mL_GCvial_ND13_10S_alignment_holder.stl
 ┃ ┃ ┃ ┣ 📜corpus_90x90mm_4mL_GCvial_ND13_10S_holder.stl
 ┃ ┃ ┃ ┣ 📜corpus_90x90mm_4mL_GCvial_ND13_1S_alignment_holder.stl
 ┃ ┃ ┃ ┣ 📜corpus_90x90mm_4mL_GCvial_ND13_1S_holder.stl
 ┃ ┃ ┃ ┣ 📜corpus_90x90mm_4mL_GCvial_ND13_4S_alignment_holder.stl
 ┃ ┃ ┃ ┣ 📜corpus_90x90mm_4mL_GCvial_ND13_4S_holder.stl
 ┃ ┃ ┃ ┣ 📜corpus_90x90mm_4mL_GCvial_ND13_6S_alignment_holder.stl
 ┃ ┃ ┃ ┣ 📜corpus_90x90mm_4mL_GCvial_ND13_6S_holder.stl
 ┃ ┃ ┃ ┣ 📜corpus_90x90mm_4mL_GCvial_ND13_8S_alignment_holder.stl
 ┃ ┃ ┃ ┣ 📜corpus_90x90mm_4mL_GCvial_ND13_8S_holder.stl
 ┃ ┗ 📂02_Corpus_130x130x130mm
 ┃ ┃ ┣ 📂00_corpus
 ┃ ┃ ┃ ┣ 📜corpus130x130mm_side_walls.stl
 ┃ ┃ ┃ ┣ 📜corpus_130x130mm_back_wall.stl
 ┃ ┃ ┃ ┣ 📜corpus_130x130mm_cover.stl
 ┃ ┃ ┃ ┣ 📜corpus_130x130mm_front_wall_monting_thermal_hose.stl
 ┃ ┃ ┃ ┣ 📜corpus_130x130mm_side_wall_left.stl
 ┃ ┃ ┃ ┣ 📜corpus_130x130mm_side_wall_right.stl
 ┃ ┃ ┃ ┣ 📜corpus_130x130mm_stand_20mm.stl
 ┃ ┃ ┃ ┣ 📜dummy.txt
 ┃ ┃ ┃ ┣ 📜fin_back_wall.stl
 ┃ ┃ ┃ ┣ 📜fin_front_wall.stl
 ┃ ┃ ┃ ┣ 📜spacer_side_walls_5mm.stl
 ┃ ┃ ┃ ┗ 📜spacer_stand_5mm.stl
 ┃ ┃ ┣ 📂01_irradiation_module
 ┃ ┃ ┃ ┣ 📜dummy.txt
 ┃ ┃ ┃ ┗ 📜irrad_module.stl
 ┃ ┃ ┣ 📂02_sample_holders
 ┃ ┃ ┃ ┣ 📜corpus_130x130mm_GCvial_ND13_18S_alignment_holder.stl
 ┃ ┃ ┃ ┣ 📜corpus_130x130mm_GCvial_ND13_18S_holder.stl
 ┃ ┃ ┃ ┣ 📜corpus_130x130mm_GCvial_ND13_1S_alignment_holder.stl
 ┃ ┃ ┃ ┣ 📜corpus_130x130mm_GCvial_ND13_1S_holder.stl
 ┃ ┃ ┗ 📂03_tempering_module
 ┃ ┃ ┃ ┣ 📜back_mounting_thermo_hose.stl
 ┃ ┃ ┃ ┣ 📜fan_holder.stl
 ┃ ┃ ┃ ┣ 📜holder_tempering_module.stl
 ┃ ┃ ┃ ┣ 📜mounting_alu_water_cooler.stl
 ┃ ┃ ┃ ┗ 📜spacer_holder_tempering_module.stl
 ┣ 📂01_controller
 ┃ ┣ 📜controller_case.stl
 ┃ ┣ 📜controller_case_LCD_holder.stl
 ┃ ┣ 📜controller_electronic_board_holder.stl
  ┗ 📂02_Peripheral_Modules
 ┃ ┣ 📂00_ambient_temperature
 ┃ ┃ ┣ 📜base_plate_ambient_temperature_extension.stl
 ┃ ┃ ┗ 📜case_ambient_temperature_extension.stl
 ┃ ┣ 📂01_tempering_extension
 ┃ ┃ ┣ 📜base_plate.stl
 ┃ ┃ ┗ 📜case_tempering_extension.stl
 ┃ ┣ 📂02_master_extension
 ┃ ┃ ┣ 📜base_plate.stl
 ┃ ┃ ┗ 📜case_master_extension.stl
 ┃ ┣ 📂03_membrane_pump_extension
 ┃ ┃ ┣ 📜base_plate_membrane_pump.stl
 ┃ ┃ ┣ 📜base_plate_membrane_pump_exension.stl
 ┃ ┃ ┣ 📜case_membrane_pump.stl
 ┃ ┃ ┗ 📜case_membrane_pump_extension.stl
 ┃ ┣ 📂04_pressure_sensor_extension
 ┃ ┃ ┣ 📜base_plate.stl
 ┃ ┃ ┗ 📜case_pressure_extension.stl
```

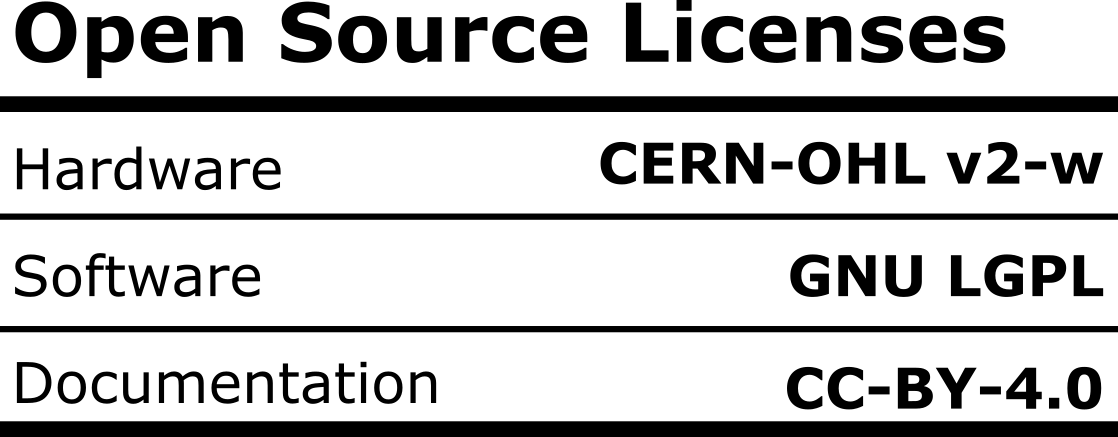
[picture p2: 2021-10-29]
04_IMAGES/Licenses.png

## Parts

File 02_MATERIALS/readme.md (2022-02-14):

# Directory Structure 
```
📦02_MATERIALS
 ┣ 📂00_electronics
 ┃ ┣ 📂00_Tinkerforge
 ┃ ┣ 📂01_LEDs
 ┃ ┃ ┣ 📂365nm
 ┃ ┃ ┃ ┣ 📜Luminus_SST-10-UV_Datasheet.pdf
 ┃ ┃ ┃ ┗ 📜Opulent_StarBoard-Horticulture-Luminus_DataSheet-1539535.pdf
 ┃ ┃ ┣ 📂385nm
 ┃ ┃ ┃ ┗ 📜LED_2520Engin_Datasheet_LuxiGen_LZ1-00UB00_rev2.1_-1531912.pdf
 ┃ ┃ ┣ 📂405nm
 ┃ ┃ ┃ ┣ 📂quadcore
 ┃ ┃ ┃ ┃ ┗ 📜LED_Engin_Datasheet_LuxiGen_LZ4_00UB0R_rev1_1_2020-1915155.pdf
 ┃ ┃ ┃ ┗ 📜LED_2520Engin_Datasheet_LuxiGen_LZ1-00UB00_rev2.1_-1531912.pdf
 ┃ ┃ ┣ 📂530nm
 ┃ ┃ ┃ ┗ 📜Opulent_StarBoard-Osram-Horticulture_DataSheet-1224877.pdf
 ┃ ┃ ┣ 📂blue
 ┃ ┃ ┃ ┣ 📂453nm
 ┃ ┃ ┃ ┃ ┗ 📜5412893_LED_2520Engin_Datasheet_LuxiGen_LZ4_00B208-2298141.pdf
 ┃ ┃ ┃ ┣ 📂455nm
 ┃ ┃ ┃ ┃ ┗ 📜Opulent_StarBoard-Horticulture_DataSheet.pdf
 ┃ ┃ ┃ ┗ 📂460nm
 ┃ ┃ ┃ ┃ ┣ 📜5412869-LED_2520Engin_Datasheet_LuxiGen_LZ1-00DB00-1532005.pdf
 ┃ ┃ ┃ ┃ ┗ 📜Herstellernummer.txt
 ┃ ┃ ┣ 📂RGBA
 ┃ ┃ ┃ ┗ 📜5412901_2520LED_2520Engin_Datasheet_LuxiGen_LZ4-00-1531987.pdf
 ┃ ┃ ┣ 📂tiefrote_740nm_LED
 ┃ ┃ ┃ ┗ 📜LED_2520Engin_Datasheet_LuxiGen_LZ4-00R308_rev1.7_-1531999.pdf
 ┃ ┣ 📂02_raspberry_pi
 ┃ ┃ ┗ 📜raspberry-pi-4-datasheet.pdf
 ┃ ┣ 📂03_sd_card
 ┃ ┃ ┗ 📜SD_card.txt
 ┃ ┣ 📂04_peltier_element
 ┃ ┃ ┣ 📜datenblatt-189115-tru-components-tec1-12706-peltier-element-15-v-64-a-65-w-l-x-b-x-h-40-x-40-x-38-mm.pdf
 ┃ ┃ ┗ 📜pelltier.txt
 ┃ ┣ 📂05_power_supplies
 ┃ ┃ ┣ 📂00_12V_5A
 ┃ ┃ ┗ 📂00_24V_6A
 ┃ ┣ 📂06_small_parts
 ┃ ┃ ┣ 📂00_stripboard
 ┃ ┃ ┗ 📂01_connection_jacks
 ┃ ┣ 📂07_LED_drivers
 ┃ ┃ ┣ 📜350mA_driver.txt
 ┃ ┃ ┣ 📜500mA_driver.txt
 ┃ ┃ ┣ 📜700mA_driver.txt
 ┃ ┃ ┗ 📜LDD-L-SPEC-1291586.pdf
 ┃ ┣ 📂08_membrane_pump
 ┃ ┃ ┣ 📜BA_FEM_-55_DE_06_161684.pdf
 ┃ ┃ ┗ 📜DB_FEM1-09_DE_178329_web_01-1.pdf
 ┃ ┗ 📂09_fans
 ┃ ┃ ┗ 📂00_photoreactor_lite_fan
 ┃ ┃ ┃ ┣ 📂00_fan_corpus_90x90mm
 ┃ ┃ ┃ ┃ ┗ 📜fan.txt
 ┃ ┃ ┃ ┣ 📂01_fan_corpus_130x130mm
 ┃ ┃ ┃ ┃ ┣ 📜fan.txt
 ┃ ┃ ┃ ┃ ┗ 📜fan_update.txt
 ┃ ┃ ┃ ┗ 📂02_power_supply_fan
 ┃ ┃ ┃ ┃ ┗ 📜power_supply.txt
 ┣ 📂01_accessories
 ┃ ┣ 📂00_thermal_tube
 ┃ ┃ ┗ 📜thermal_hose.txt
 ┃ ┣ 📂01_hose_clamps
 ┃ ┃ ┗ 📜hose_clamp.txt
 ┃ ┣ 📂02_screws_nuts
 ┃ ┃ ┣ 📂00_M3_Set
 ┃ ┃ ┃ ┗ 📜M3_screw_set.txt
 ┃ ┃ ┣ 📂01_Nylon_Spacer
 ┃ ┃ ┃ ┗ 📜nylon_spacer.txt
 ┃ ┃ ┗ 📂02_M3_70mm
 ┃ ┃ ┃ ┗ 📜M3_70mm.txt
 ┃ ┣ 📂03_cooler
 ┃ ┃ ┣ 📂00_tempering_module_cooler
 ┃ ┃ ┃ ┣ 📂00_pelltier_cooler
 ┃ ┃ ┃ ┃ ┗ 📜spec_sheet_Alpine_AM4_Passive_180321_r1_DE.pdf
 ┃ ┃ ┃ ┗ 📂01_alu_water_cooler
 ┃ ┃ ┃ ┃ ┗ 📜alu_water_cooler.txt
 ┃ ┃ ┗ 📂01_LED_cooler
 ┃ ┃ ┃ ┣ 📂00_25mm_cooler
 ┃ ┃ ┃ ┃ ┗ 📜sink_s-1265491.pdf
 ┃ ┃ ┃ ┗ 📂01_50mm_cooler
 ┃ ┃ ┃ ┃ ┗ 📜sink_s-1265491.pdf
 ┃ ┗ 📂04_foam_rubber_seal
 ┃ ┃ ┗ 📜foam_rubber_seal.txt
 ┗ 📜readme.md
```

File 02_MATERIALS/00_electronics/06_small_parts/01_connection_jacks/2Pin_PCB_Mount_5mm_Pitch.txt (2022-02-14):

Hersteller/Manufacturer: 	FULARR 
AISN ‏ : ‎ B07PQVXCH4 
Herstellerreferenz/Manufacturer reference:	 	AK3-AT1-GL-M-X 
Verkäufer/Supplier: Amazon
size: 8.0 x 10.0 x 10.0 mm
link: https://www.amazon.de/-/en/QitinDasen-80pcs-Premium-Terminal-Connector/dp/B07PQVXCH4/ref=sr_1_10?crid=22XIER4WR2DBJ&dchild=1&keywords=anschluss+platine+5%2C08+mm&qid=1635519383&qsid=257-2331300-1205907&sprefix=anschluss+platine+5.08+mm%2Caps%2C73&sr=8-10&sres=B07RDG39LT%2CB07S2GF264%2CB082ZNRQMJ%2CB07PPRYT4X%2CB085RSJLM7%2CB083GNB8BY%2CB07PQVXCH4%2CB00NWEC8TW%2CB00GWF65WY%2CB07BDKG68Q%2CB08K32Q9Y9%2CB0728HZHTR%2CB06XRBKSY2%2CB079FKG2M2%2CB0734XYJPM%2CB077VVKN1R%2CB073B4WQHD%2CB0716WZ6RW%2CB08G1BSP8D%2CB01GKWC7C0

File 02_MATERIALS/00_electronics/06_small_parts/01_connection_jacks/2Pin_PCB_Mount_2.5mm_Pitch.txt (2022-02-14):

Hersteller/Manufacturer: 	Walfront 
EAN ‏ : ‎ 0711632969480 
ASIN ‏ : ‎ B07YQYRKC5 
Herstellerreferenz/Manufacturer reference:	 	Walfronts7g90oct3i 
Verkäufer/Supplier: Amazon
size: 12 x 6.3 x 5.5 mm
link: https://www.amazon.de/dp/B07YQYRKC5/ref=sspa_dk_detail_3?psc=1&pd_rd_i=B07YQYRKC5&pd_rd_w=70OKJ&pf_rd_p=4f2ceb27-95e9-46ab-8808-db390b56ec01&pd_rd_wg=KIDz2&pf_rd_r=NCA7ZMZJPW94Z8MSF698&pd_rd_r=ec069438-50b3-4c69-84ea-63f7dd16dfa8&smid=A5QX2SUPA7LK7&spLa=ZW5jcnlwdGVkUXVhbGlmaWVyPUEzQ09DTUJQSTA2MDBEJmVuY3J5cHRlZElkPUEwMTExNjIyTUZIVjZDR0QzUTVFJmVuY3J5cHRlZEFkSWQ9QTAxNTUyNTAzMEJZSTVMMlNPNUcwJndpZGdldE5hbWU9c3BfZGV0YWlsJmFjdGlvbj1jbGlja1JlZGlyZWN0JmRvTm90TG9nQ2xpY2s9dHJ1ZQ==

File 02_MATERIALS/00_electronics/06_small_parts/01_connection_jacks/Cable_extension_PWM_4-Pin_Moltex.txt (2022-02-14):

Hersteller/Manufacturer: 	 	‎InLine
ASIN ‏ : ‎ B005IEUDAU 
Herstellerreferenz/Manufacturer reference:	 	33328 
Verkäufer/Supplier: Amazon

link: https://www.amazon.de/InLine-L%C3%BCfterkabel-Verl%C3%A4ngerung-Stecker-Buchse/dp/B005IEUDAU/ref=pd_sbs_7/257-2331300-1205907?pd_rd_w=5WGqM&pf_rd_p=b1c388c3-48c2-4960-8532-fa8f1477aee9&pf_rd_r=6CCP2EVQWN886SZ7CT4S&pd_rd_r=c8d34dbd-a124-4ca3-ad34-ad7884668d0f&pd_rd_wg=QNmuc&pd_rd_i=B005IEUDAU&th=1

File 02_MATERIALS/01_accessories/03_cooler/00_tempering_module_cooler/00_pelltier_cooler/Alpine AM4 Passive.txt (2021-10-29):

Hersteller/Manufacturer: 	arctc
Herstellerreferenz/Manufacturer reference:	 	Alpine AM4 Passive
size: 95x95x69mm
Verkäufer/Supplier: arctic
link: https://www.arctic.de/alpine-am4passive
link data sheet: https://www.arctic.de/media/9b/f4/1b/1584096716/spec_sheet_Alpine_AM4_Passive_180321_r1_DE.pdf

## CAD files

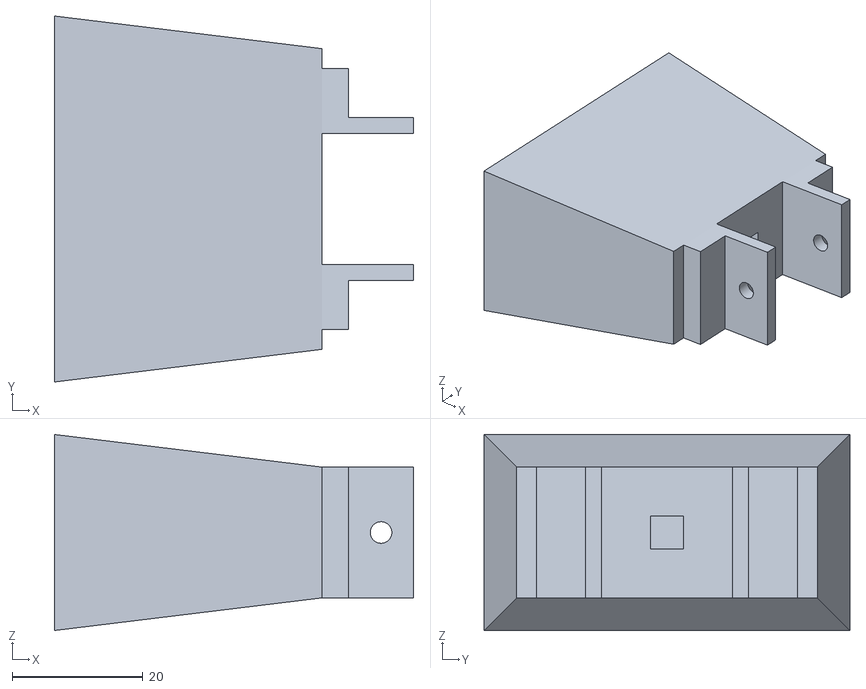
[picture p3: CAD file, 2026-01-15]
01_CAD/03_Multi_Batch_Screening_Photoreactor/01_Direct_Irradiation_Module/00_reflector_fixed_height/holder_feet_assembly.stl
55.0 x 56.0 x 30.0

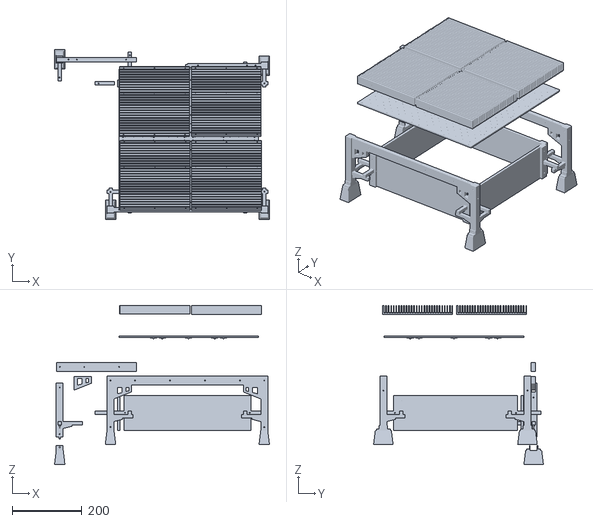
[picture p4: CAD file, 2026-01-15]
01_CAD/03_Multi_Batch_Screening_Photoreactor/01_Direct_Irradiation_Module/00_reflector_fixed_height/reflector_fixed_height_assembly.stl
615.3 x 486.2 x 456.2

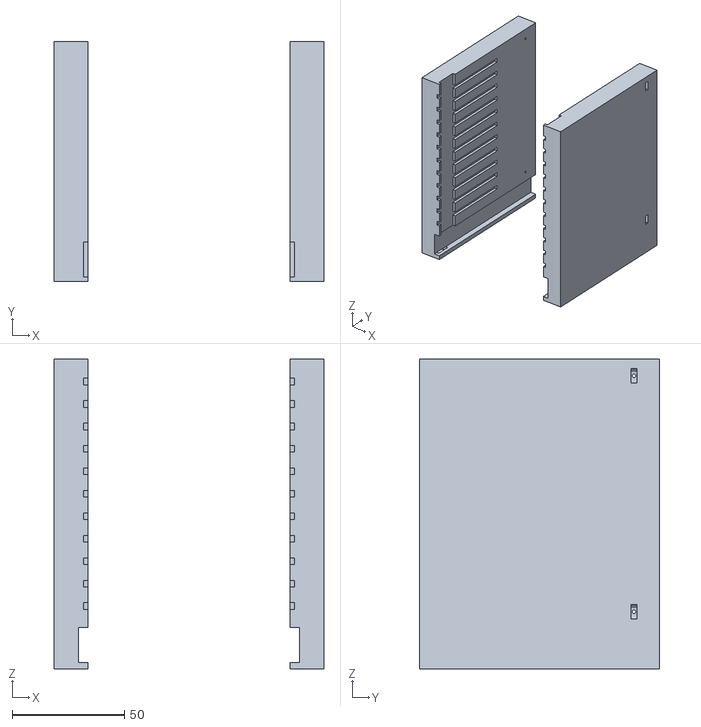
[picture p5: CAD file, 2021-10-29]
01_CAD/00_Corpus/00_Corpus_90x90x100mm/00_corpus/corpus_90x90x100mm_side_walls.stl
120.0 x 106.7 x 138.0

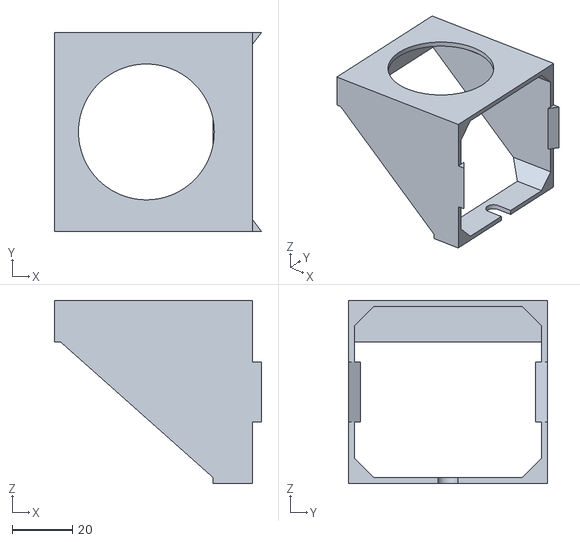
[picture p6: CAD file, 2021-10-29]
01_CAD/00_Corpus/00_Corpus_90x90x100mm/01_irradiation_module/corpus_90x90mm_irrad_Max350_adapter.stl
68.6 x 65.9 x 60.7

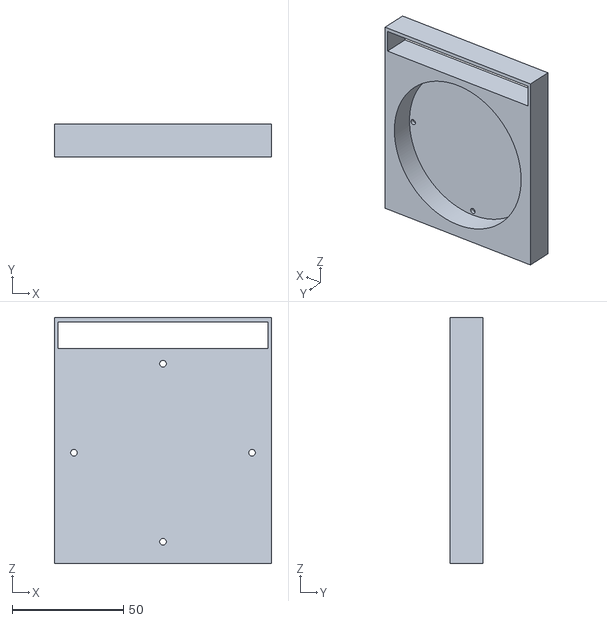
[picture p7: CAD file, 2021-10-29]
01_CAD/00_Corpus/00_Corpus_90x90x100mm/02_stirring_module/corpus_90x90mm_stirring_module.stl
97.5 x 15.0 x 110.5

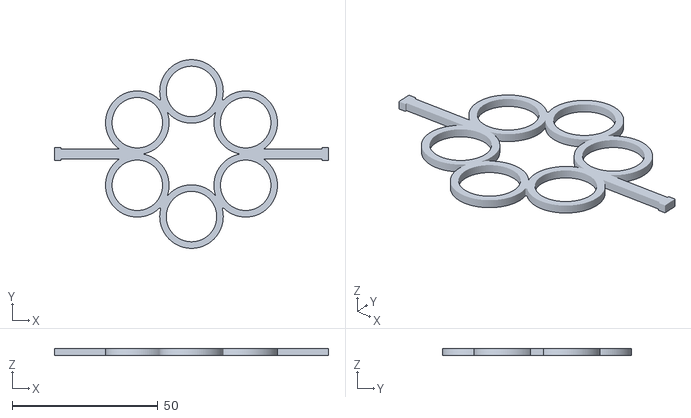
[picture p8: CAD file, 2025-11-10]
01_CAD/00_Corpus/00_Corpus_90x90x100mm/03_sample_holders/corpus_90x90mm_11mL_Biotage_MWvial_6S_alignment_holder.stl
94.0 x 64.7 x 2.40

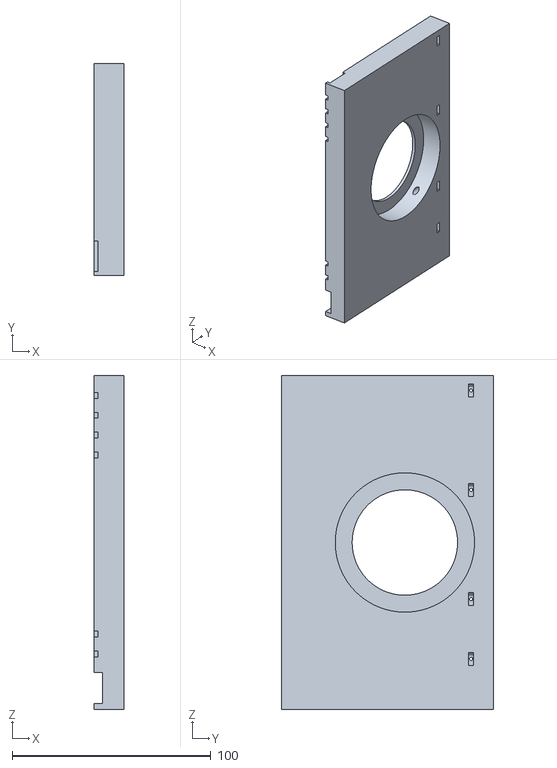
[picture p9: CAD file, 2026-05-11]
01_CAD/00_Corpus/01_Corpus_90x90x140mm/00_corpus/corpus_90x90x140mm_side_wall_solar_simulator_LOT-Quantum_Design_LSH302.stl
15.0 x 106.7 x 168.0

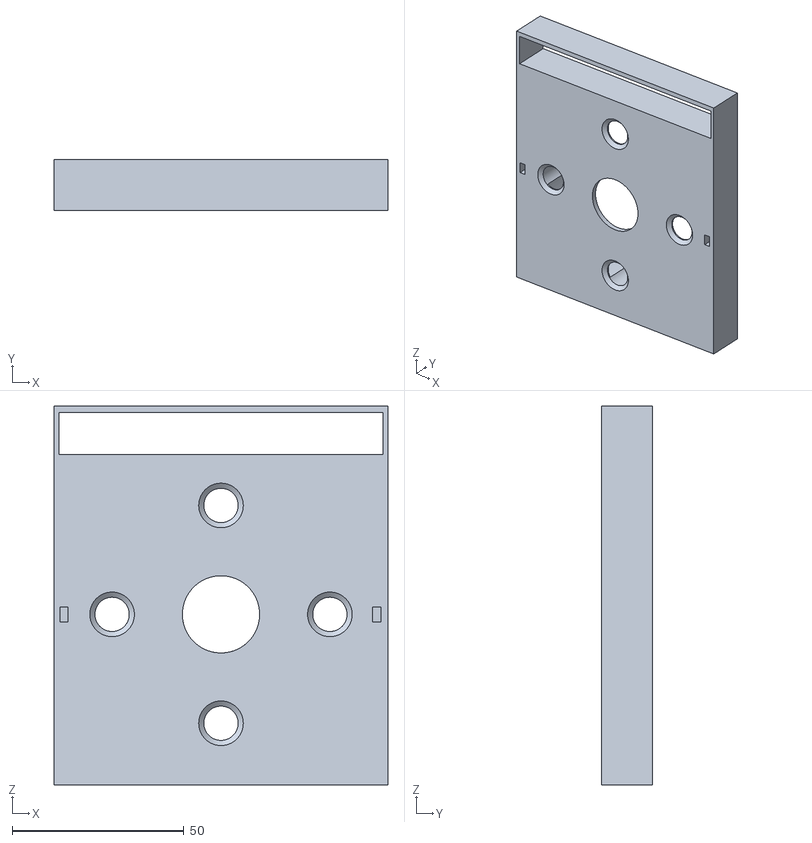
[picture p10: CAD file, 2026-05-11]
01_CAD/00_Corpus/01_Corpus_90x90x140mm/01_irradiation_module/corpus_90x90mm_irrad_starcool.stl
97.3 x 14.9 x 110.5

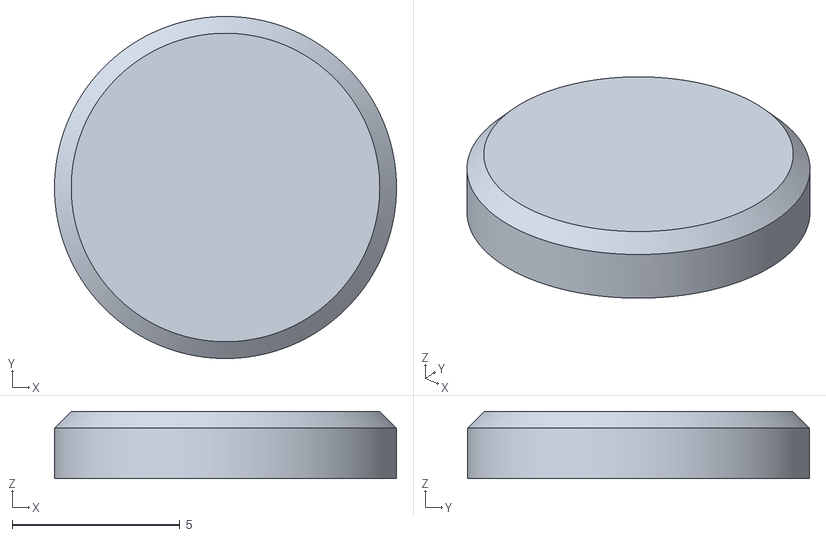
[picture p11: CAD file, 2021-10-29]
01_CAD/00_Corpus/01_Corpus_90x90x140mm/02_stirring_module/corpus_90x90mm_stirring_module_magnet_holder_blind_plug.stl
10.2 x 10.2 x 2.00

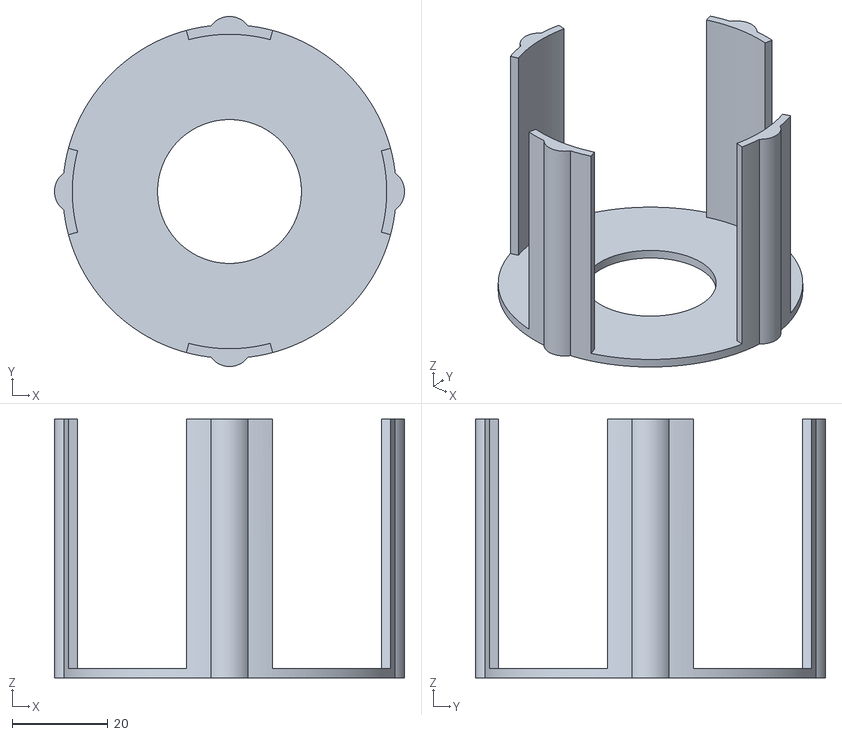
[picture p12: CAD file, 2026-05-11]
01_CAD/00_Corpus/01_Corpus_90x90x140mm/03_sample_holders/corpus_90x90mm_bottom_holder_Schott_GL45_100mL.stl
73.0 x 73.0 x 54.0

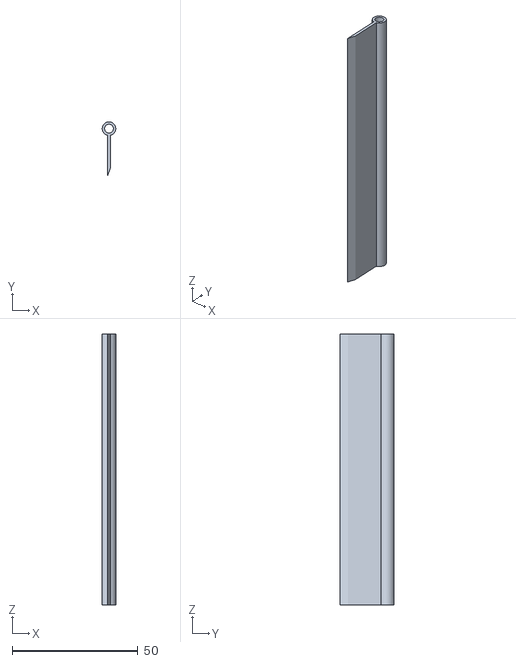
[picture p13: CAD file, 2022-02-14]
01_CAD/00_Corpus/02_Corpus_130x130x130mm/00_corpus/fin_back_wall.stl
5.40 x 21.6 x 107.7

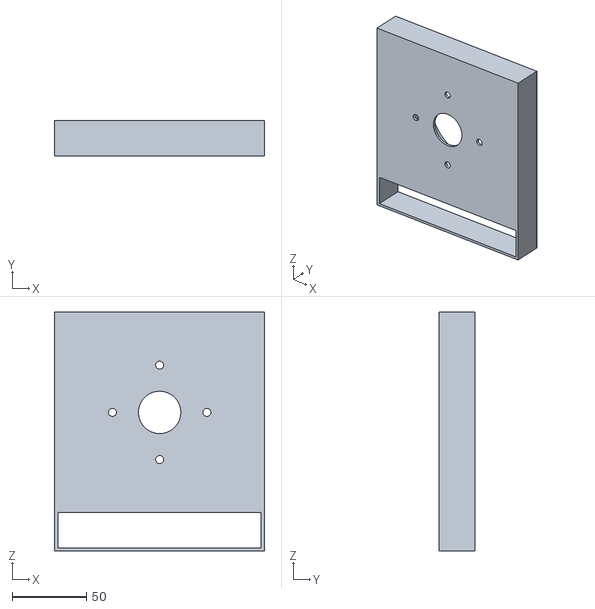
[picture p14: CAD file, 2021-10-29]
01_CAD/00_Corpus/02_Corpus_130x130x130mm/01_irradiation_module/irrad_module.stl
141.3 x 24.0 x 160.8

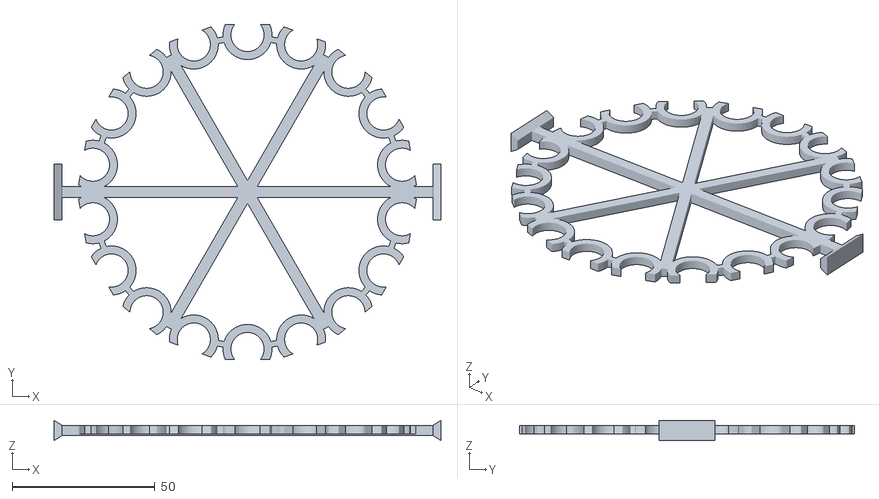
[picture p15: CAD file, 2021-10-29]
01_CAD/00_Corpus/02_Corpus_130x130x130mm/02_sample_holders/corpus_130x130mm_GCvial_ND13_18S_holder.stl
135.6 x 117.5 x 7.10

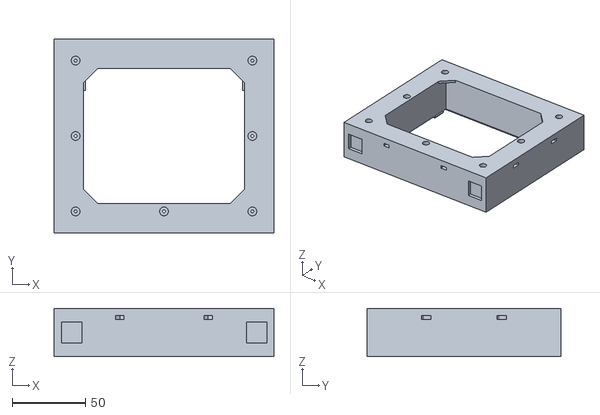
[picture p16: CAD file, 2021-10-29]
01_CAD/00_Corpus/02_Corpus_130x130x130mm/03_tempering_module/fan_holder.stl
150.2 x 132.5 x 33.1

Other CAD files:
01_CAD/01_controller/controller_case.stl
01_CAD/02_Peripheral_Modules/00_ambient_temperature/case_ambient_temperature_extension.stl
01_CAD/02_Peripheral_Modules/01_tempering_extension/base_plate.stl
01_CAD/02_Peripheral_Modules/02_master_extension/case_master_extension.stl
01_CAD/00_Corpus/00_Corpus_90x90x100mm/00_corpus/corpus_90x90x100mm_back_wall.stl
01_CAD/00_Corpus/00_Corpus_90x90x100mm/00_corpus/corpus_90x90x100mm_front_wall.stl
01_CAD/00_Corpus/00_Corpus_90x90x100mm/00_corpus/corpus_90x90x100mm_side_walls_LED_holder.stl
01_CAD/00_Corpus/00_Corpus_90x90x100mm/00_corpus/corpus_cover.stl
01_CAD/00_Corpus/00_Corpus_90x90x100mm/00_corpus/corpus_stand.stl
01_CAD/00_Corpus/00_Corpus_90x90x100mm/01_irradiation_module/20210104_Thorlabsl_modul.stl
01_CAD/00_Corpus/00_Corpus_90x90x100mm/01_irradiation_module/corpus_90x90mm_irrad_Max350.stl
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

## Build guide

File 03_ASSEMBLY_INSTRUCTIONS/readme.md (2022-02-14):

# Diretory Structure
```
📦03_ASSEMBLY_INSTRUCTIONS
 ┣ 📂00_Corpus
 ┃ ┣ 📜Assembly_Photoreactor_Corpus_130x130x130mm.pdf
 ┃ ┣ 📜Assembly_Photoreactor_Corpus_90x90x140mm.pdf
 ┃ ┗ 📜Assembly_Photoreactor_Corpus_90x90x90mm.pdf
 ┣ 📂01_Controller
 ┃ ┣ 📜Controller_Documentation.pdf
 ┃ ┣ 📜Controller_Documentation.svg
 ┃ ┣ 📜Logic_Controller.pdf
 ┃ ┣ 📜Logic_Controller.svg
 ┃ ┗ 📜Logic_Controller.vsdx
 ┣ 📂02_Peripheral_Modules
 ┃ ┗ 📂00_Tempering_Module
 ┃ ┃ ┣ 📜Peltier_Circuit_Diagram.pdf
 ┃ ┃ ┗ 📜Peltier_Circuit_Diagram.svg
 ┣ 📂03_Irradiation_Module
 ┃ ┗ 📜assembly_instruction_LED_cooler.pdf
 ┗ 📜readme.md
```

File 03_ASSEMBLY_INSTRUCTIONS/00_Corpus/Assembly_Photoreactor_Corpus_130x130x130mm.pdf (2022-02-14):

setPageBoxes("Crop", 0, 0, [0,2000,2000,0]);

# Modular Photoreactor Assembly Instructions

TITLE | INSTRUCTIONS

Assembly of the Photoreactor Corpus 130x130x130mm

ORGANIZATION

Institute of Chemical
Engineering Ulm University
DESIGNER | Daniel Kowalczyk
1) LED Module assembly: slide the cooler with mounted LED into the 3D-printed holder. Fix the cooler with 4 M3 screws (length adjusted to the thickness of the cooler) and 4 M3 nuts as shown in the depiction of the setup.
2) Fixation of the ventilation fins: place the fins of the right length in the front and back part of the corpus fixed by each 8 M3 (length: 30 mm and 40 mm) screws.
3) Make sure to cut out foam sealings for every surface connecting the 3D-printed parts. This ensures sufficient tempering of the setup.
4) Corpus assembly: place 8 M3 nuts in the slits of the side parts of the corpus. Fix the back part of the corpus with 8 M3 (length: 30 mm) according to the graphical assembly instruction.
5) Assembly of the tempering module: The peltier elements must be connected in a row according to (A-B-C-D). Make sure to put heat conducting paste between all interfaces to assure sufficient heat conduction. Place the peltier elements A and B on top of the passive alumina cooler. Stack C and D on A and B according to the 3D graph. Make sure that each heating and cooling side of the Peltier elements face the same direction. Place the alumina water cooler on top of C and D. Cut a piece of the foam sealing to the dimensions of the water cooler (40x80mm) and place it on top of the cooler. Slide the whole tempering unit into the 3D-printed holder. Fix the alumina passive holder in place using the 3D-printed spacer. Fix the water cooler from the top using the four slotted screws delivered with the alumina passive cooler. Place the 15 M3 nuts into the slits of the 3D-printed holder. Fix the assembled tempering module with 8 M3 screws from the inside of the corpus (length: 30 mm).
6) Assembly of the fan module: fix the fan with four M3 screws (length: 30 mm) and four M3 nuts according to the 3D-graphic. Make sure the air flow is directed into the tempering module. Place 8 M3 nuts in the slits of the 3D-printed fan holder. Fix the fan module to the tempering module using 7 M3 screws (length: 30 mm).
7) Fixation of the tempering air inlet: fix the 3D-printed inlet using 8 M3 screws (length: 30 mm). Connect the tempering air inlet with the tempering air outlet using the thermoinsulated tubing with the hose clamps.

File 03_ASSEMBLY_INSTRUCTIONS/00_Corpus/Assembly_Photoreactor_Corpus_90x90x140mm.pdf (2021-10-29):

setPageBoxes("Crop", 0, 0, [0,2000,2000,0]);

# Modular Photoreactor Assembly Instructions

TITLE | INSTRUCTIONS

Assembly Instruction
Photoreactor Corpus
90x90x140mm

ORGANIZATION

Institute of Chemical
Engineering Ulm University
DESIGNER | Daniel Kowalczyk
1) LED Module assembly: slide the cooler with mounted LED into the 3D-printed holder. Fix the cooler with 4 M3 screws (length adjusted to the thickness of the cooler) and 4 M3 nuts as shown in the depiction of the setup.
2) Corpus assembly: place 6 M3 nuts in the slits of the side parts of the corpus. Fix the back part of the corpus with 4 M3 screws (length: 30 mm) according to the graphical assembly instruction. Fix the fan (120x120mm) to the back part of the corpus with 4 M3 screws (length: 70 mm) according to the graphical assembly instruction.

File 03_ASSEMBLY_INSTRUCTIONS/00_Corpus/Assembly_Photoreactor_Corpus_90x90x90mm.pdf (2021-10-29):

setPageBoxes("Crop", 0, 0, [0,2000,2000,0]);

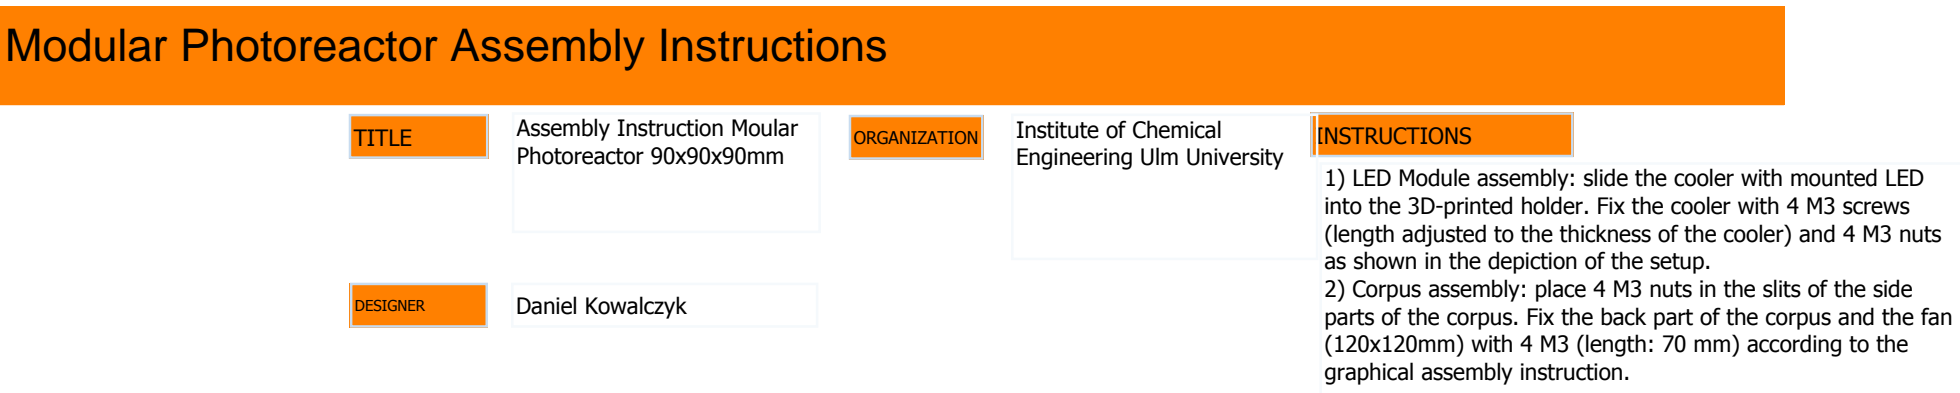
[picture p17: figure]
TITLE; INSTRUCTIONS; Assembly Instruction Moular Photoreactor 90x90x90mm; ORGANIZATION; Institute of Chemical Engineering Ulm University; DESIGNER; Daniel Kowalczyk; as shown in the depiction of the setup.; graphical assembly instruction.

# Modular Photoreactor Assembly Instructions

1) LED Module assembly: slide the cooler with mounted LED into the 3D-printed holder. Fix the cooler with 4 M3 screws (length adjusted to the thickness of the cooler) and 4 M3 nuts
2) Corpus assembly: place 4 M3 nuts in the slits of the side parts of the corpus. Fix the back part of the corpus and the fan (120x120mm) with 4 M3 (length: 70 mm) according to the

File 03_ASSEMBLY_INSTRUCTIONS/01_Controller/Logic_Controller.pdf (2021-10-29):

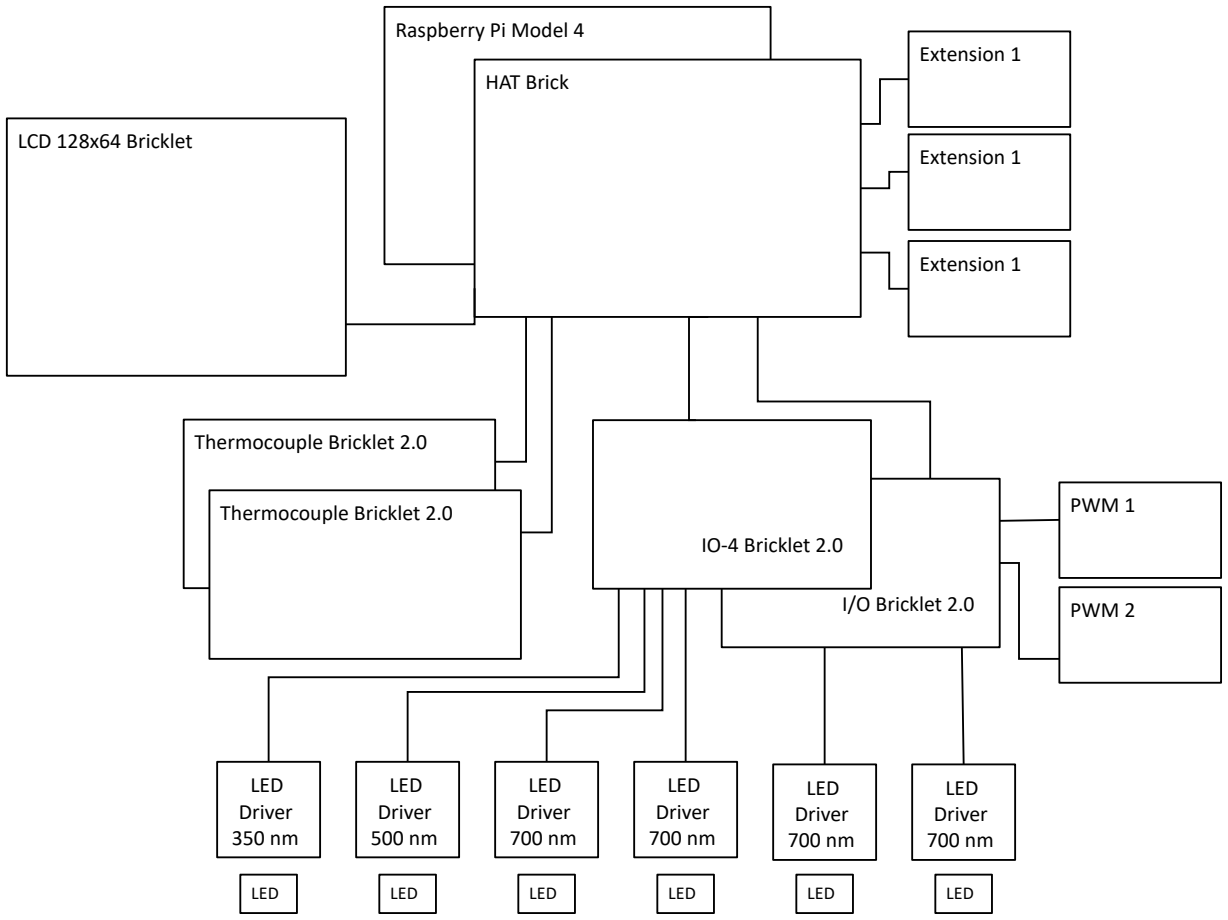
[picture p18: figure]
Raspberry Pi Model 4; HAT Brick; Thermocouple Bricklet 2.0; LED Driver 350 nm; LED; LED Driver 500 nm; LED Driver 700 nm; I/O Bricklet 2.0; IO-4 Bricklet 2.0; LCD 128x64 Bricklet; PWM 1; PWM 2; Extension 1

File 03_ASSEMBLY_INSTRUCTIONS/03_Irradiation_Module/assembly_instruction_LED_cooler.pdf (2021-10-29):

setPageBoxes("Crop", 0, 0, [0,2000,2000,0]);

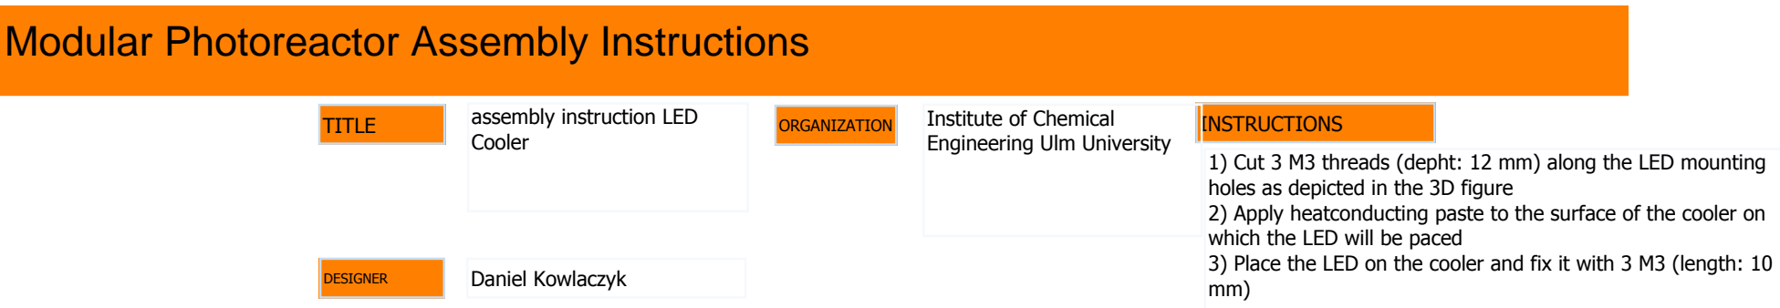
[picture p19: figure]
TITLE; INSTRUCTIONS; assembly instruction LED Cooler; ORGANIZATION; Institute of Chemical Engineering Ulm University; DESIGNER; Daniel Kowlaczyk; holes as depicted in the 3D figure; which the LED will be paced

# Modular Photoreactor Assembly Instructions

1) Cut 3 M3 threads (depht: 12 mm) along the LED mounting
2) Apply heatconducting paste to the surface of the cooler on
3) Place the LED on the cooler and fix it with 3 M3 (length: 10

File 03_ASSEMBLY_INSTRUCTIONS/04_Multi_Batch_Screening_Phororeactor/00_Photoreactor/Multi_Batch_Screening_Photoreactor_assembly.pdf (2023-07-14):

setPageBoxes("Crop", 0, 0, [0,2000,2000,0]);

# Assembly Instructions

TITLE

Multi-Batch Screening
Photoreactor

ORGANIZATION

Institute of Chemical
Engineering Ulm University | INSTRUCTIONS DESIGNER | Daniel Kowalczyk
1) placement of the base modules: The base module is clipped to the the corresponding openings of the IKA Roller 10.
2) assembly of the irradiation module: The used SMD mounted LEDs can be fixed to the 300 mm aluminum heat sinks at variable positions in 20 mm steps. The LEDs are mounted at the precut heat sink threads (M3) using 2 M3 (5 mm) screws. The used LEDs are connected in a row, a 1 A fuse is incorporated in front of every module to protect the LEDs from higher currents. The irradiation modules are connected to the power supply using 4 mm banana plugs. The heat sink holder is mounted using 2 M3 (5 mm) screws.
placement of the irradiation module: The irradiation module stand is fixed tor the heat sink holder using 2 M3 (25 mm) screws and corresponding nuts. After the assembly of the irradiation module is finished it can be clipped to the installed base module.
3) assembly of the reflector module: The PTFE side walls are mounted to the reflector holder using 4 M3 (8 mm) screws and corresponding nuts. The PTFE reflector is placed within the guideway of the reflector holder. The two reflector holder parts are connected using 4 M3 (10 mm) screws and corresponding nuts.
placement of the irradiation module: The reflector module is clipped on top of the irradiation modules.

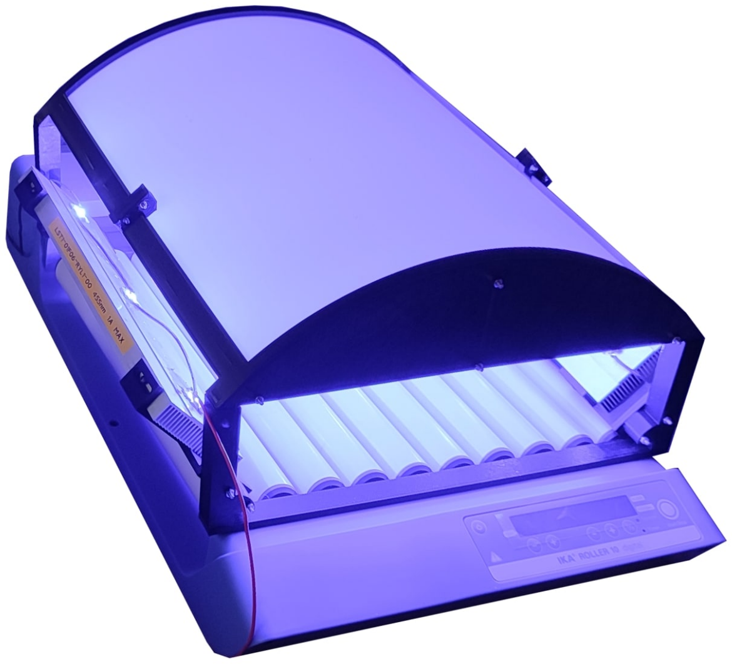
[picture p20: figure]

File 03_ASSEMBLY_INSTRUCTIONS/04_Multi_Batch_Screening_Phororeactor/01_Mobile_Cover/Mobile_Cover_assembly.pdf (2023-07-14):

setPageBoxes("Crop", 0, 0, [0,2000,2000,0]);

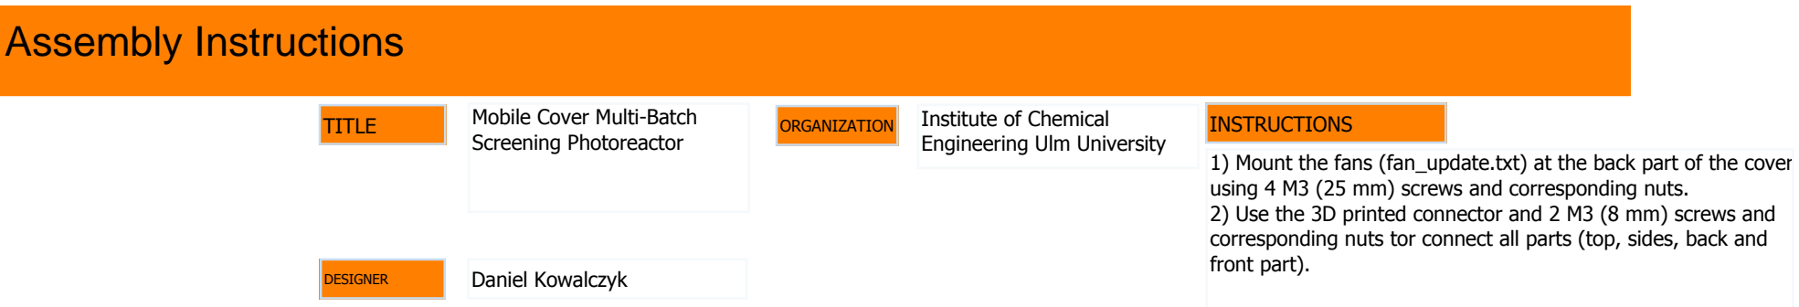
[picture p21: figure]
Assembly Instructions; TITLE; Mobile Cover Multi-Batch Screening Photoreactor; ORGANIZATION; Institute of Chemical; front part).

Engineering Ulm University | INSTRUCTIONS DESIGNER | Daniel Kowalczyk
1) Mount the fans (fan_update.txt) at the back part of the cover using 4 M3 (25 mm) screws and corresponding nuts.
2) Use the 3D printed connector and 2 M3 (8 mm) screws and corresponding nuts tor connect all parts (top, sides, back and

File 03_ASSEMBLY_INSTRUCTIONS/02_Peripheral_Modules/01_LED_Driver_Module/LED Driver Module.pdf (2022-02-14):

## LED Driver Module

### Parts:

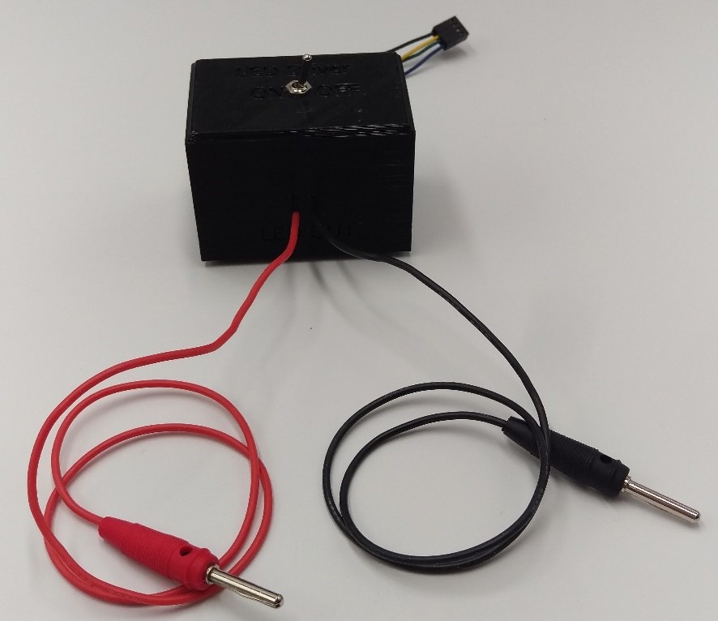
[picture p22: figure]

- LED Driver (LDD-L-SPEC-1291586)
- Two position switch
- Silicone wire
- Cable extension PWM 4-Pin Moltex
- Red banana plug
- black banana plug
- 3D printed LED diver case
- 3D printed base plate
- 3D printed LED driver holder
- 4 x 10 mm nylon spacer
- 4 x M3 nylon nuts
- 4 x M3 steel nuts
- 8 x M3 8 mm steel screws

### Assembly Instructions

1) Connect the banana plugs to the wires and place them inside of the holes (LED out) in the 3D printed case. Cut the Cable extension PWM 4-Pin Moltex cables approximately at half of their length. Take the female side of the Cable extension PWM 4-Pin Moltex and place the 4 Cables in the 4 holes of the 3D printed case.
2) Insert the two-position switch between the yellow wire of Cable extension PWM 4-Pin Moltex. Therefore, cut the yellow cable in half and put the switch in between. Connect the two-position switch with -VIN of the LED driver. Fit the switch at the hole on the top of the 3D printed case. Connect the yellow to +VIN and the blue wire to PWM. Connect the black and red wires of the

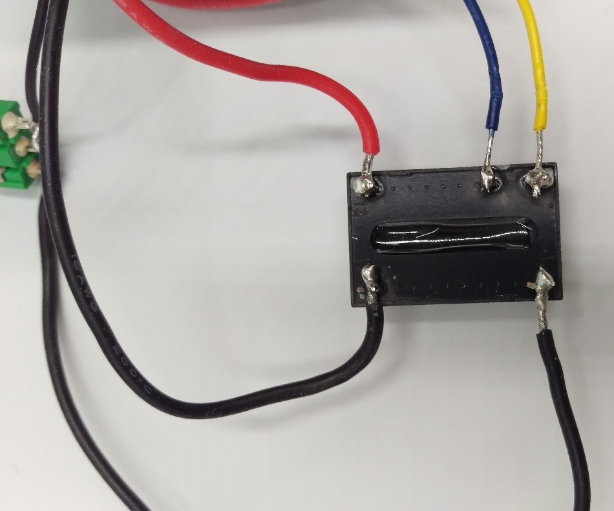
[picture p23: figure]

LED out connectors to -VOUT and +VOUT.

3) Fix the nylon spacers to the LED Driver holder using the nylon nuts. Fix this assembly to the base plate using 4 M3 8 mm screws. Push the LED driver gently into the holder until you feel a resistance.
O +VOUT | O PWM O +VIN
O -VOUT | O -VIN

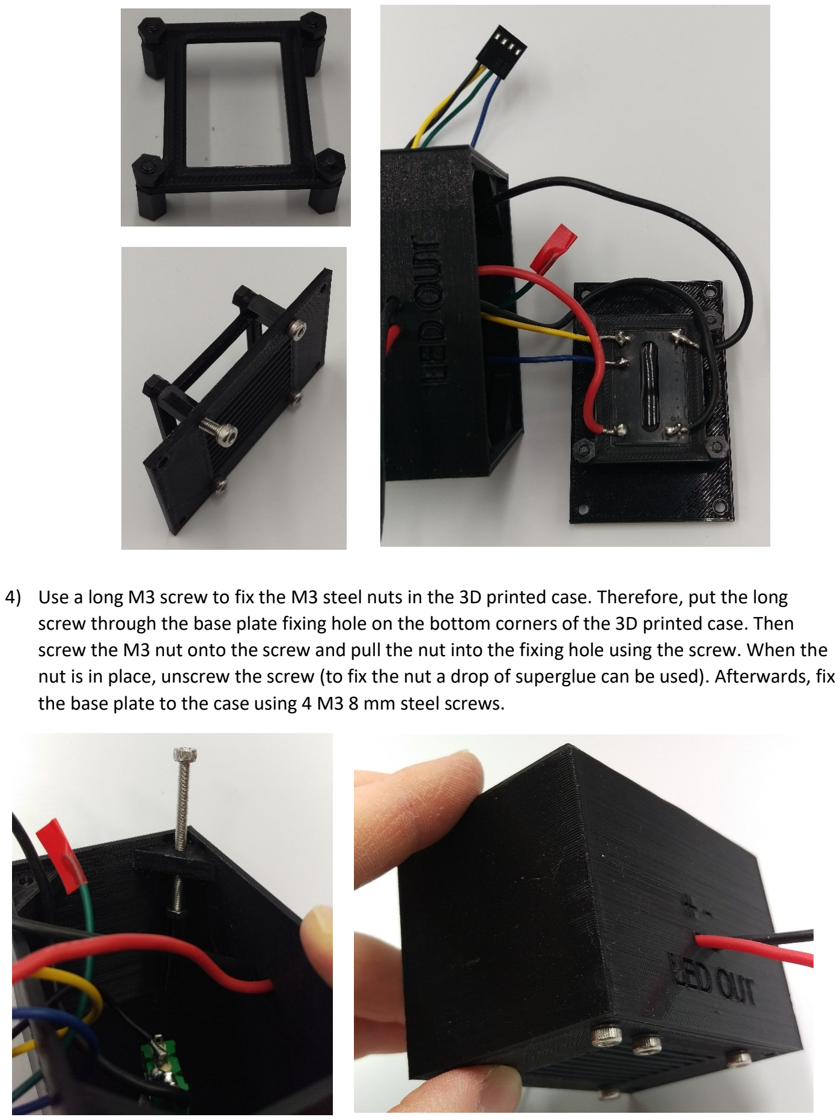
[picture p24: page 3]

4) Use a long M3 screw to fix the M3 steel nuts in the 3D printed case. Therefore, put the long screw through the base plate fixing hole on the bottom corners of the 3D printed case. Then screw the M3 nut onto the screw and pull the nut into the fixing hole using the screw. When the nut is in place, unscrew the screw (to fix the nut a drop of superglue can be used). Afterwards, fix the base plate to the case using 4 M3 8 mm steel screws.

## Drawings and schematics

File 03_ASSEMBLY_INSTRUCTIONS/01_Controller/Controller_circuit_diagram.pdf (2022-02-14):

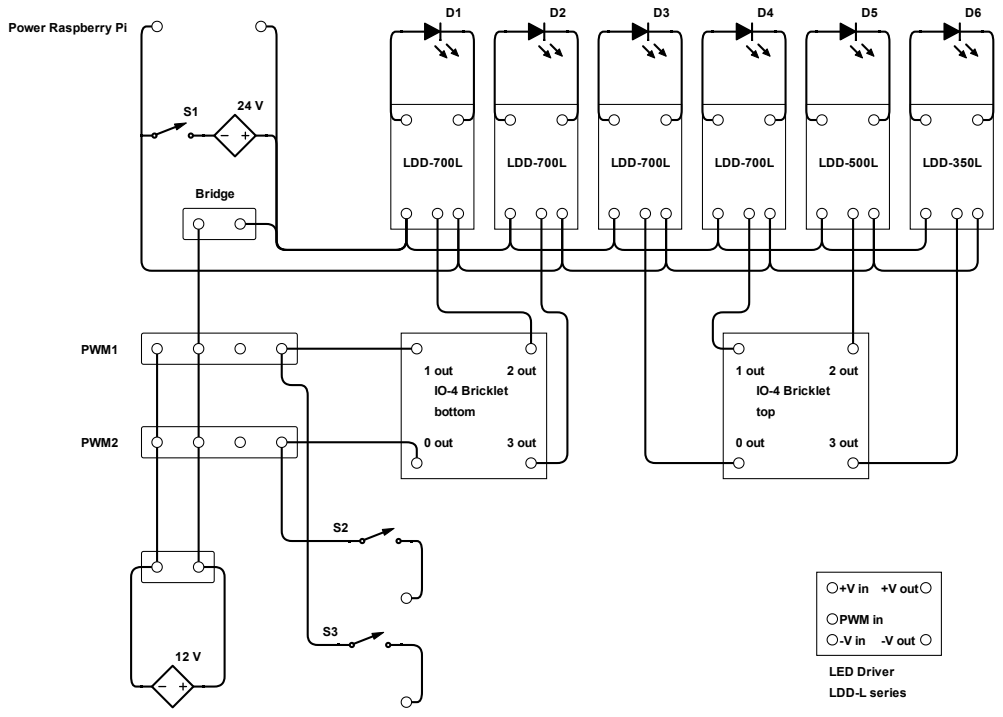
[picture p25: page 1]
LDD-700L; LDD-500L; LDD-350L; IO-4 Bricklet top; IO-4 Bricklet; 0 out; 1 out; 2 out; 3 out; bottom; PWM in; +V out; -V out; LDD-L series; LED Driver; Bridge; PWM1; PWM2

Power Raspberry Pi

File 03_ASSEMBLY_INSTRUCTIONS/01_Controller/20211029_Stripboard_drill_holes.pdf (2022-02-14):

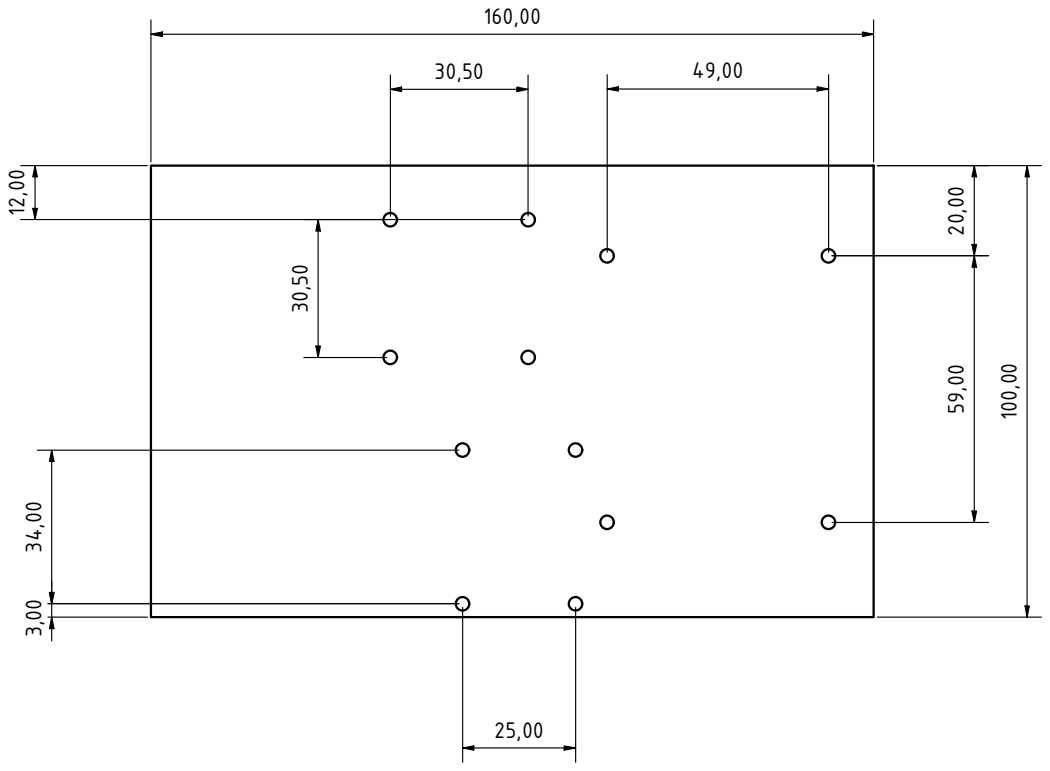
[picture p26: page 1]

Datum | Name

Gezeich | 29.10.2021 | Daniel

Kontroll

Norm

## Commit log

2022-02-14 made software available as a package added full software documentation added further instructions for assemblies added additional information on parts
    [fin_back_wall.stl]
2023-07-14 - refactoring: separating hardware and software - software is now stored here: Py4ModPhotoreactor - added Multi Batch Screening Photoreactor
    [20210104_Thorlabsl_modul.stl, 300mm_alu_heatsink.stl, Base_Module.stl, PTFE_Side_Wall.stl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]
2025-11-10 Add .stl files for Biotage Microwave Vial Holders
    [corpus_90x90mm_11mL_Biotage_MWvial_6S_alignment_holder.stl, corpus_90x90mm_11mL_Biotage_MWvial_6S_holder.stl]
2026-01-15 Add Direct Irradiation Module to CAD Multi-Batch Screening Photoreactor
    [300mm_alu_heatsink.stl, Base_Module.stl, LED_mount_400x400.stl, PTFE_Side_Wall.stl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]
2026-05-11 Delete 01_CAD/00_Corpus/01_Corpus_90x90x140mm/01_irradiation_module/corpus_90x90mm_irrad_starcool.stl
    file deleted
    [corpus_90x90mm_irrad_starcool.stl]
2026-05-11 Add files via upload
    add updated file
    [corpus_90x90mm_irrad_starcool.stl]
2026-05-11 Add files via upload
    added new module for side irradiation with LEDs
    [corpus_90x90x140mm_side_walls_LEDs_starcool.stl]
2026-05-11 Add files via upload
    added side irradiation module for the LOT-Quantum Design LSH302 compact solar simulator
    [corpus_90x90x140mm_side_wall_solar_simulator_LOT-Quantum_Design_LSH302.stl]
2026-05-11 Add files via upload
    add holders for GL45 100 mL SCHOTT bottle
    [corpus_90x90mm_1_vial_holder_Schott_GL45_100mL.stl, corpus_90x90mm_bottom_holder_Schott_GL45_100mL.stl]
